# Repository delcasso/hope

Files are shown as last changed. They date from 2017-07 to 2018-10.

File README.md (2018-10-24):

# Welcome to the HOPE project GitHub Page

Here we present and share the full design of a new brain implant.
We believe this implant will be benificial for the community as it is, open-source, cheap, easy to build, easy to modify via CAD software, and 3D printable.

The website is still under construction, please don't hesitate to ask what you need at sebastien.delcasso@gmail.com

To start, look at the [paper](https://www.frontiersin.org/articles/10.3389/fncir.2018.00041/full) and the [contruction protocol](https://github.com/delcasso/hope/blob/master/HOPE%20construction-implantation%20procedure_SD_20180416-1355.pdf).

<br />This work is licensed under a <a rel="license" href="http://creativecommons.org/licenses/by-nc-nd/4.0/">Creative Commons Attribution-NonCommercial-NoDerivatives 4.0 International License</a>.

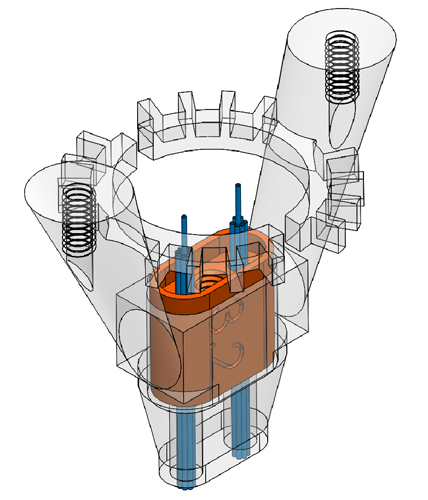
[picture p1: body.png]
body


**Figure 1:** Schematic Representation of HOPE implant

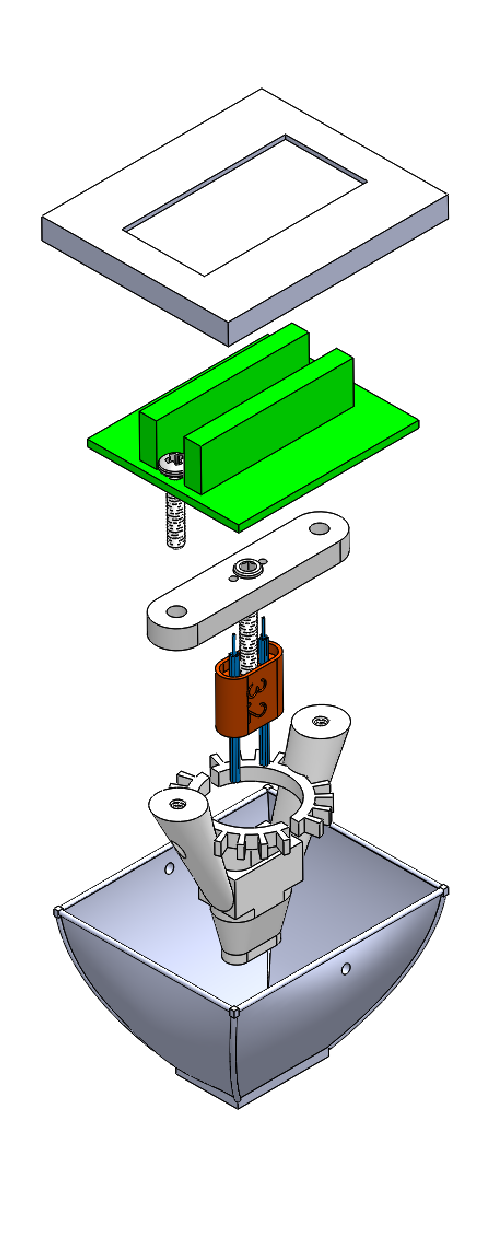
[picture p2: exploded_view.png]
exploded view


**Figure 2:** Exploded View of HOPE implant

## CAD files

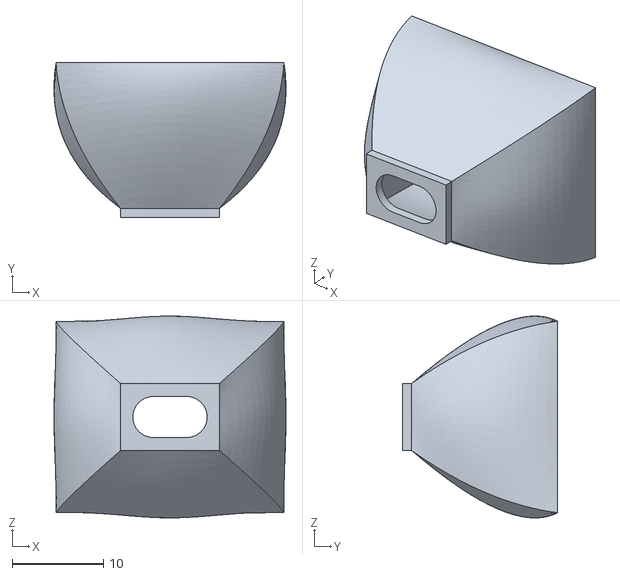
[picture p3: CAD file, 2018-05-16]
CapBottom_20170710.STL
25.4 x 17.0 x 22.2

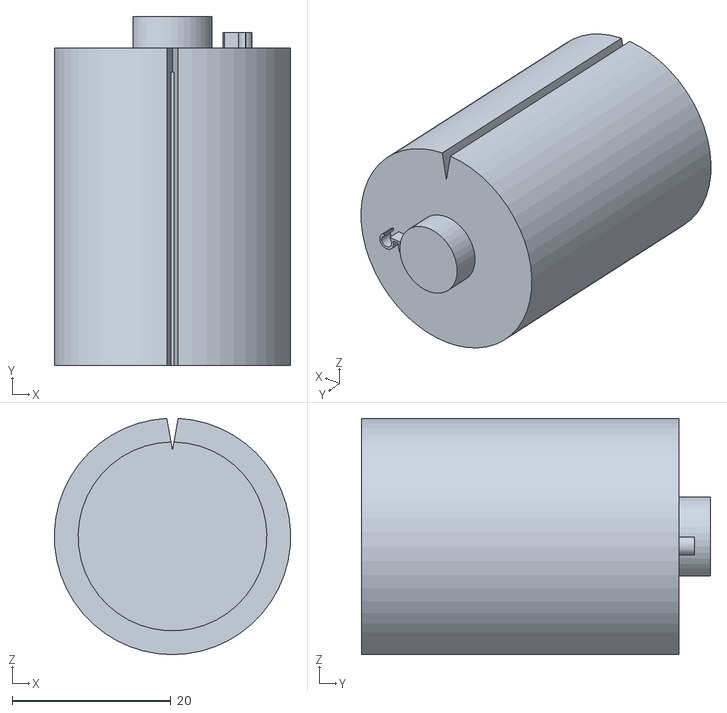
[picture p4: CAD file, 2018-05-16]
length 5mm TetrodeAdjustementPLate^all_20170707.STL
29.8 x 44.0 x 29.8

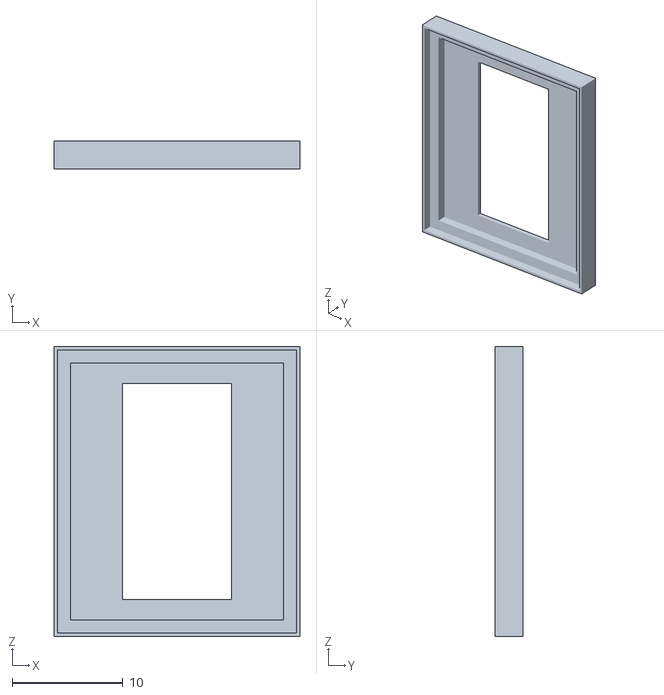
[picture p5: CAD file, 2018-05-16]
CapTop 20170101.STL
22.2 x 2.50 x 26.2

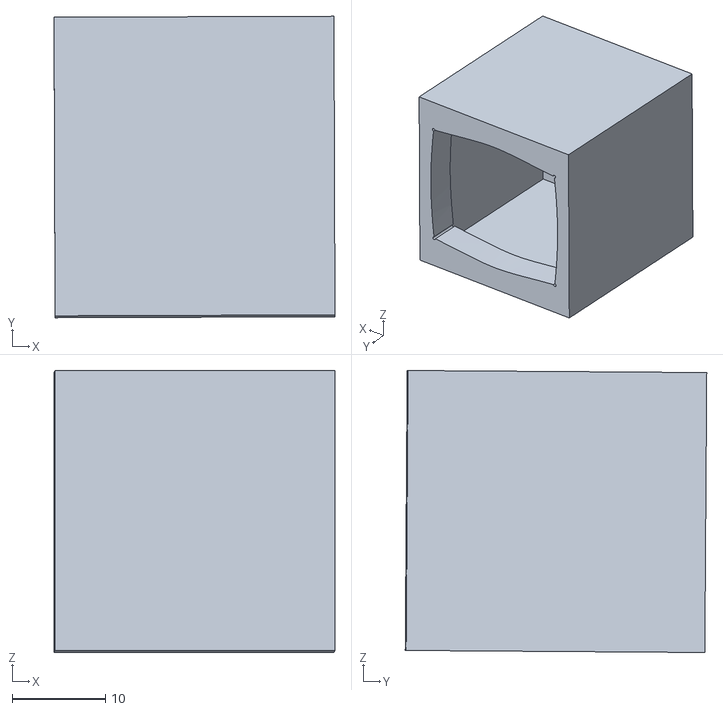
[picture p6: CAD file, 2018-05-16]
StorageBox_20170103.STL
30.1 x 32.3 x 30.2

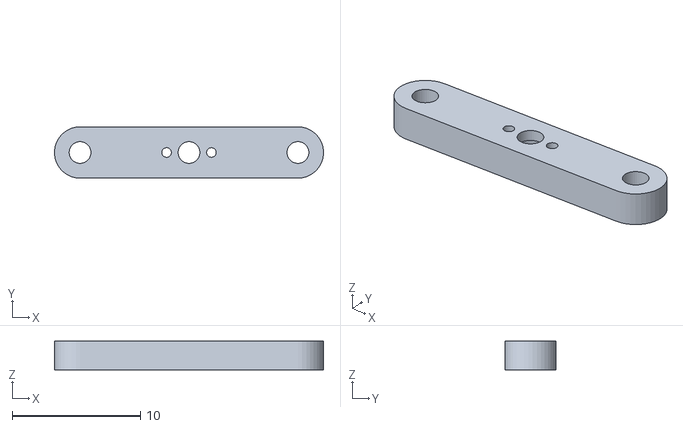
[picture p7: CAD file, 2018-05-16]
Bar_20170101.STL
21.0 x 4.00 x 2.25

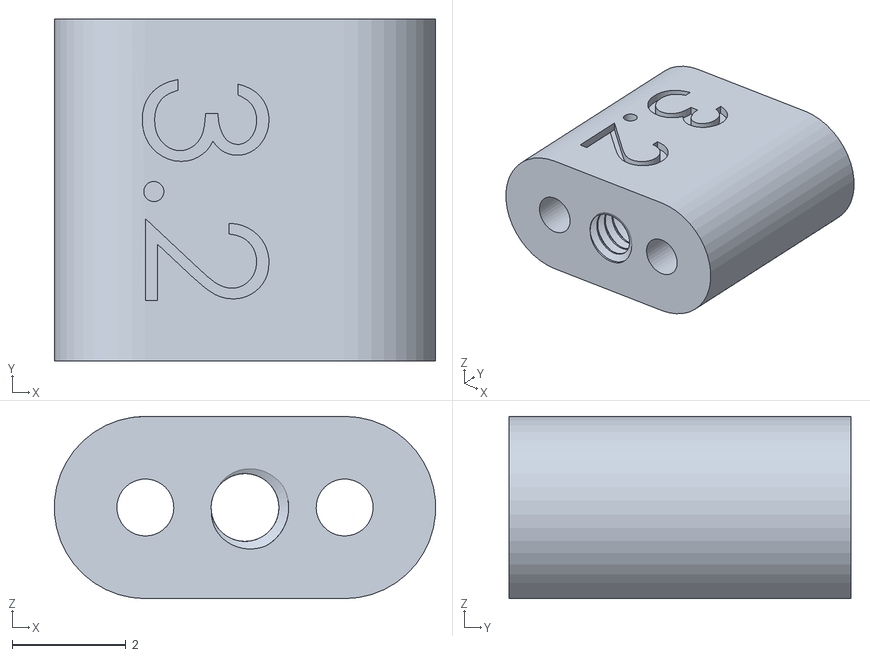
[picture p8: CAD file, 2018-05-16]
3.2 Shuttle.STL
6.69 x 6.00 x 3.20

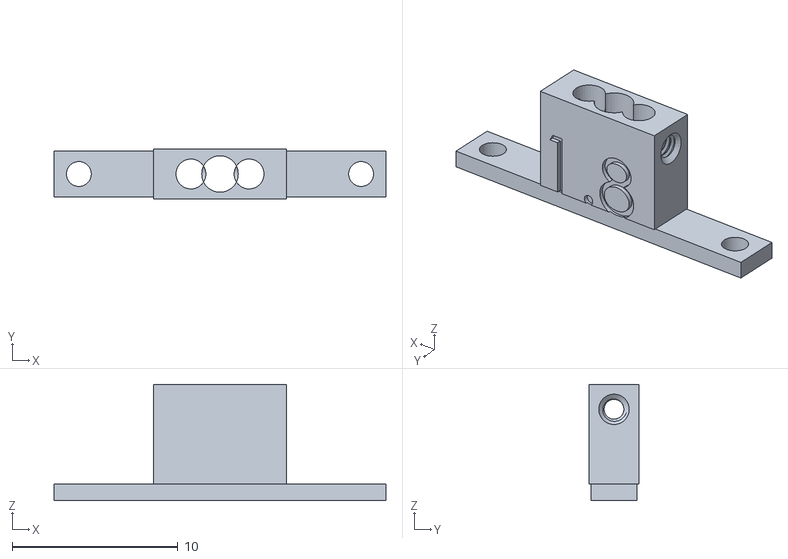
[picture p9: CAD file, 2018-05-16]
FiberHolder 7mm 1.8mm^Assem1.STL
20.0 x 3.00 x 7.00

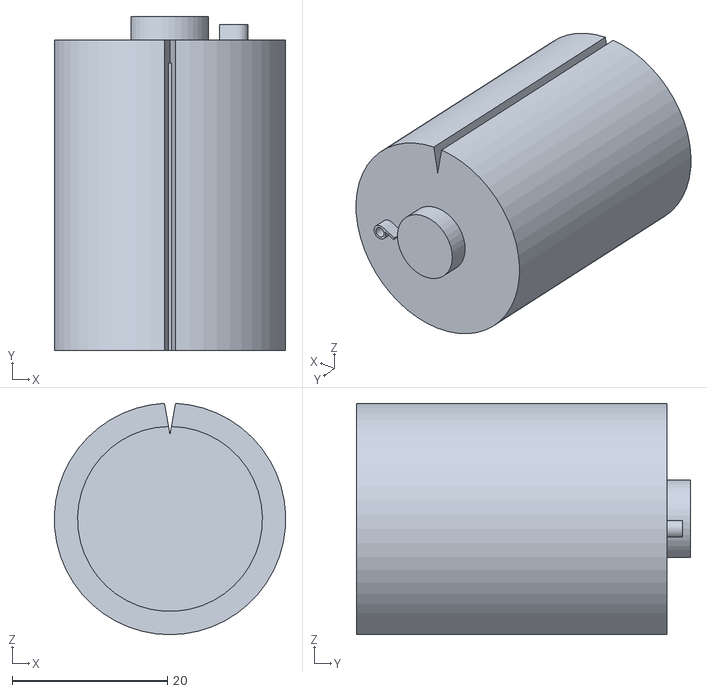
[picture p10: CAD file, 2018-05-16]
length 6mm TetrodeAdjustementPLate^all_20170707.STL
29.8 x 43.0 x 29.8

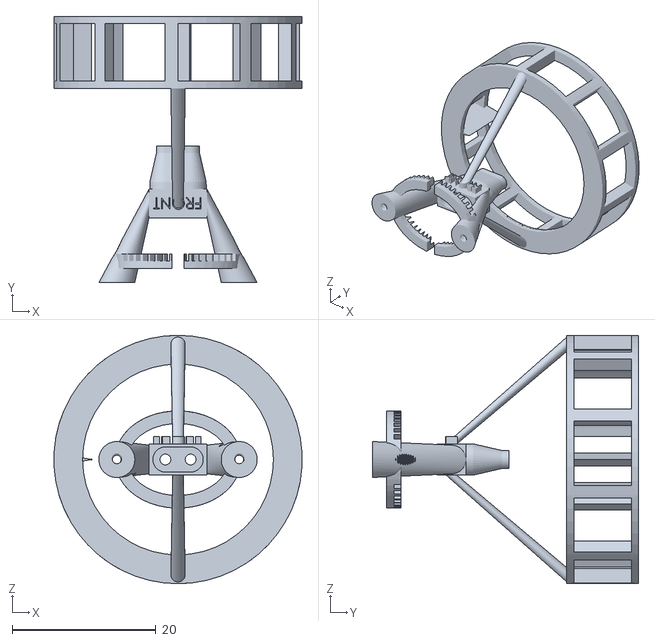
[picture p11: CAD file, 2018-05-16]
Body-With-Stand_20170711.STL
34.4 x 37.0 x 34.5

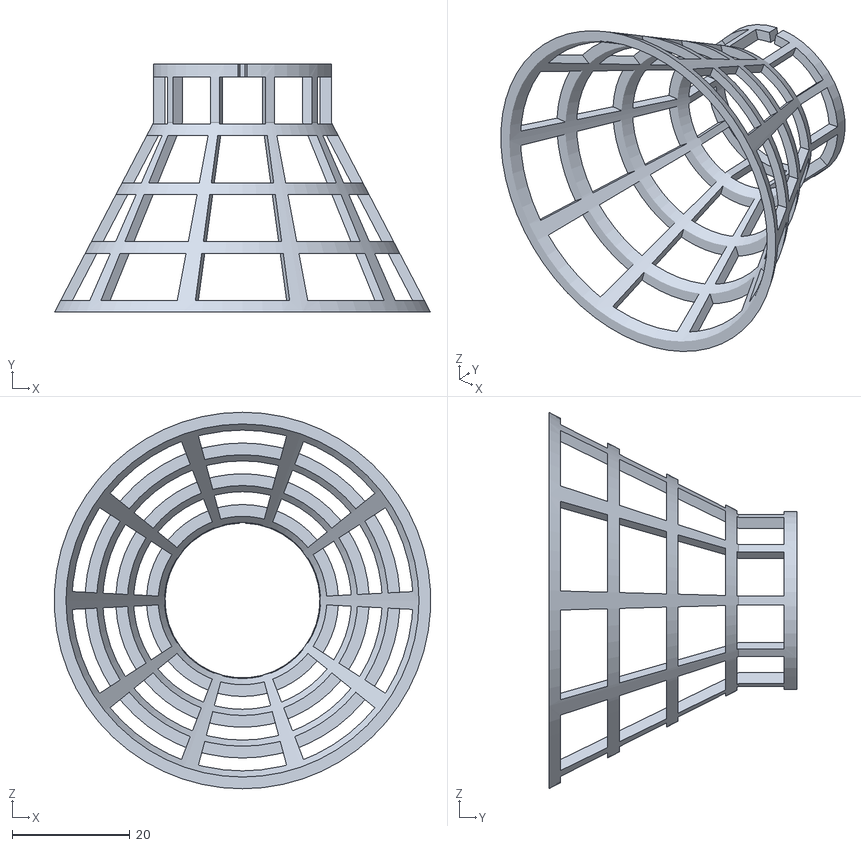
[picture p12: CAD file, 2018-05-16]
TT_loading_stand_20170117.STL
63.9 x 42.2 x 64.0

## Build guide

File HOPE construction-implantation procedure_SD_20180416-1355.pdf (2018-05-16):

FABRICATION OF THE HOPE DRIVE https://delcasso.github.io/hope/

TETRODE FABRICATION

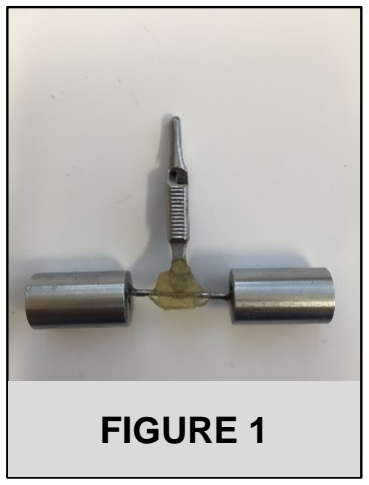
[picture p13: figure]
FIGURE 1

1. Wash your hands.
2. Cut a 30 cm section of 20 µm diameter tungsten wire using serrated scissors.
3. Fold the wire in half and run your fingers along the length of the wire to stick the strands together. Deionized water can be applied if necessary to keep the strands together.
4. Cut the extremity of the loop.
5. Fold the wire in half again to form a loop on one end and cut the tips of the wires on the other end to ensure that they are aligned.
6. Clip the four ends together using an alligator clip that has been modified with a horizontal bar and weights (Figure 1).
7. Hang the wire directly above a turning device and place the bar of the alligator clip into the tetrode spinner (Figure 2).
8. Apply 115 clockwise turns followed by 15 counterclockwise turns.
9. Melt the insulation of the wires to fuse them together. Use a heat gun at the highest temperature setting (1000°F) to heat the wire from four different directions.
10. For each direction, move the heat gun back and forth along the length of
the wire twice at a distance of 1-2 cm, spending approximately 4
seconds on each pass.

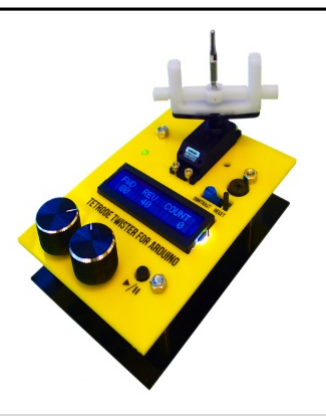
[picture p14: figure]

11. Lift the alligator clip slightly to release the tension from the weights and cut the tetrode above the tip of the alligator clip. Transfer the new tetrode into an anti-static box for storage.

You can consult the following JoVE link for a video that describe the procedures for tetrode construction. https://www.jove.com/video/1098/micro-drive-array-for-chronic-in-vivo-recording-tetrode-assembly (https://www.jove.com/video/1098/micro-drive-array-for-chronic-in-vivo-recording-tetrode-assembly)

### FIGURE 2

SHUTTLE ASSEMBLY

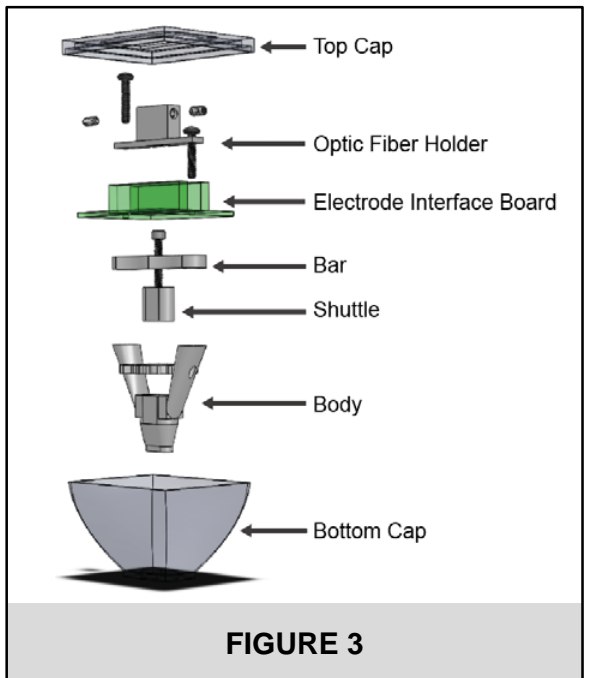
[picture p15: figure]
FIGURE 3

1. Remove all parts from the 3D printer (Figure 3)
2. Remove supports from 3D printed parts (Figures 4 and 5).
3. The shuttle needs to slide smoothly and should be tight inside the body. The shuttle can be sanded down once on each side to ensure a proper fit.
4. Also check that the tetrode adjustment block fit fully within the ring of the body (Figure 6).
5. Use an 0-80 tap to form threads along:
a. the central hole of the shuttle (Figure 7)
b. the two EIB posts on the body
c. the two holes in the side of the body’s shuttle chamber
When you tap the hole, it is not good to try to go all the way in. When it becomes too difficult to turn, it is better to unscrew the tapping tool and blow in the hole.
6. Cut eighteen sections of M-tube (0.0062”/0.0092” ID/OD), each 12 mm in length, with a razor blade.
7. Insert 9 of these segments into both the left and right holes of the shuttle. If you plan to use optical fibers, then cut two more sections of M-tube, each 15 mm in length. Place on long M-tube in the center of each bundle (Figure 8). Optic fibers will be glued inside the middle tube when the bundle will be assembled. If you plan to perform drug injection, place an injection cannula at the center of the bundle. The injection cannula is usually located 500 µm above the tip of the tetrodes.
8. Adjust the position of the M-tubes until they protrude 5.5 mm from the bottom of the shuttle.
9. Apply drops of a light-curing adhesive around the M-tubes using a needle and cure with UV light (405 nm) for 10 seconds. Make sure to wear appropriate glasses to protect your eyes from UV light.
10. Ensure that no adhesive falls into the tapped central hole.
a. It may be easier to make one bundle first and then the other one.

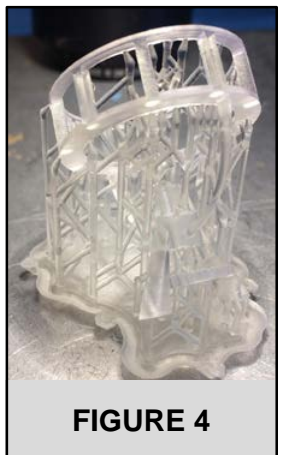
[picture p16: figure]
FIGURE 4
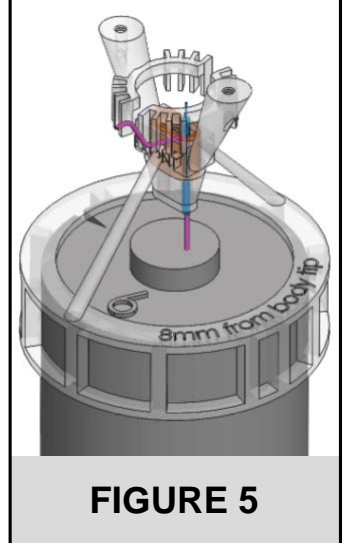
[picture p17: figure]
FIGURE 5
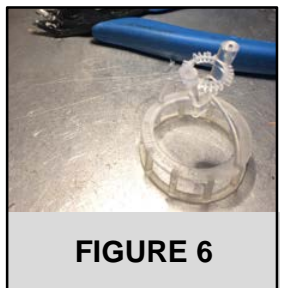
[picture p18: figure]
FIGURE 6
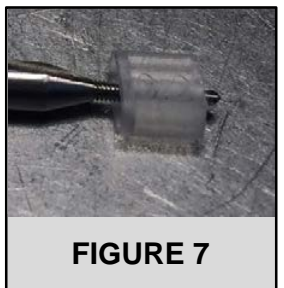
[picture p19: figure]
FIGURE 7

b. Use a needle with epoxy and apply to M-tubes where they exit the base of the shuttle so that the epoxy travels by capillary action up into the shuttle hole and around M-tubes.
c. Apply down about ¾ the length of the M-tubes to ensure each M-tube is secured in the bundle.
11. If necessary, adhesive can be applied slightly above the bottom of the M-tubes to hold them together in a tight cluster. Ensure that no adhesive enters through the bottom of the M-tubes and cure with UV light for 10 seconds. You can also use a second shuttle to hold the tip of the bundle when you are gluing it.

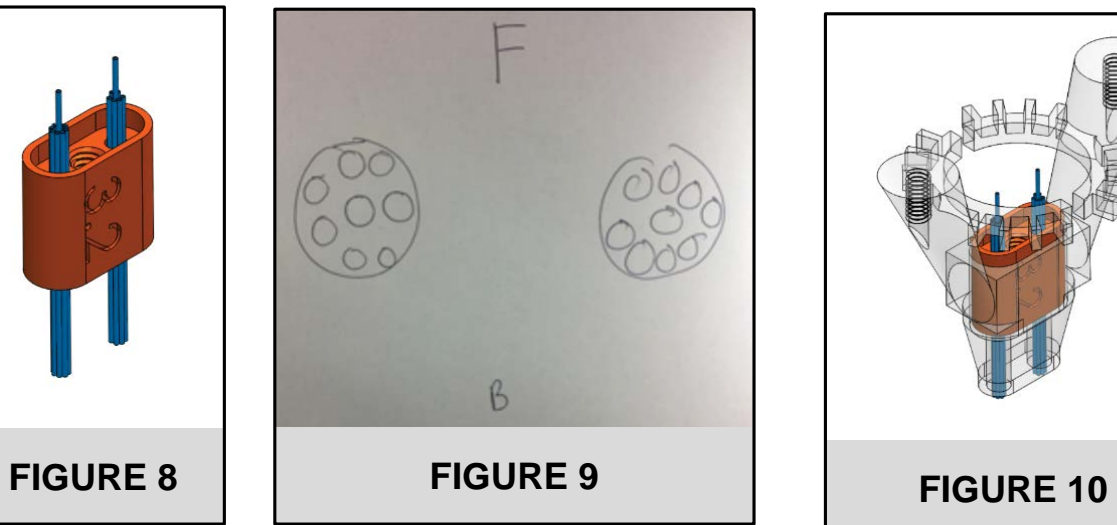
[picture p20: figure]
FIGURE 10 FIGURE 8; FIGURE 9
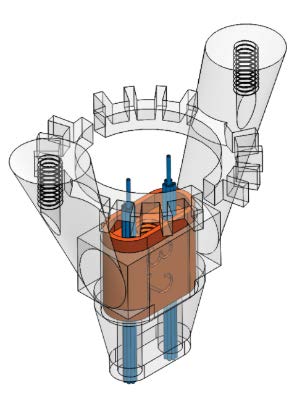
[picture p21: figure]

12. Draw exactly what you see (Figure 9) and label the front side with F (both on the diagram and on the shuttle itself)
13. Use the tap to guide the bottom of the shuttle into the body, making sure that the M-tubes slide through the holes in the drive body without bending. Make sure the shuttle is fully inserted into the body (Figure 10).
14. In preparation for loading tetrodes, with a fine needle (26G), test whether each M-tube is glued in place and does not slide down by touching lightly on the top of each. You can also use a needle to open any compressed M-tube openings.

TETRODE INSERTION

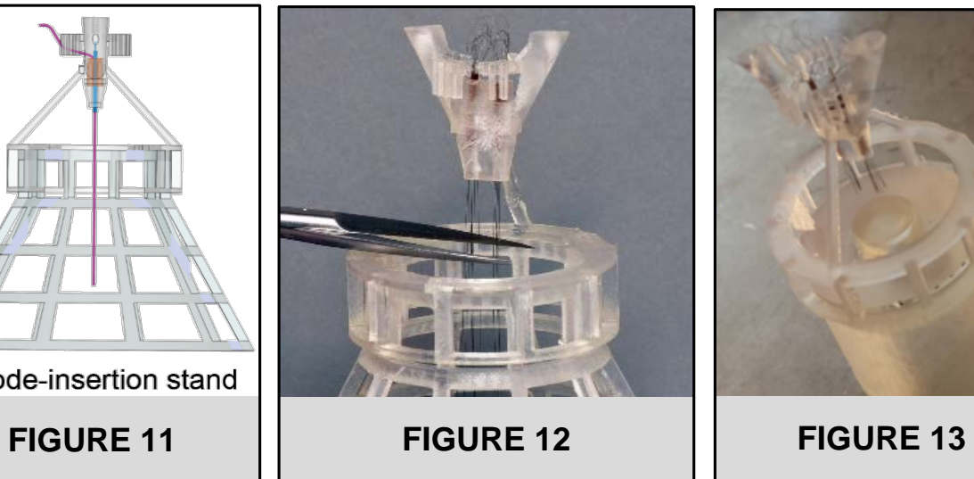
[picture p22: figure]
FIGURE 11; FIGURE 12; FIGURE 13
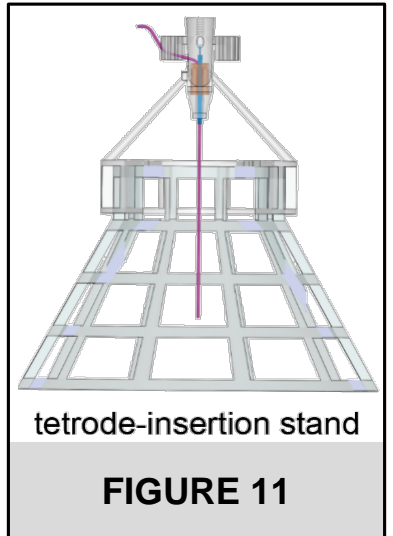
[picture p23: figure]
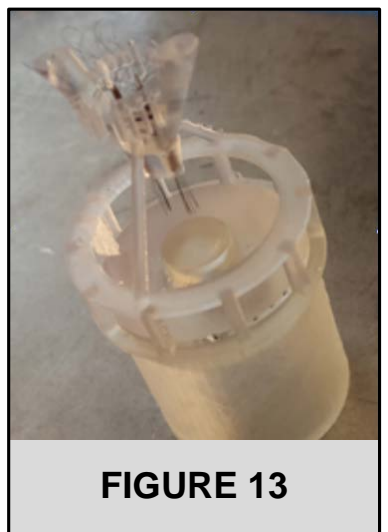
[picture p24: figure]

1. Place drive body into tetrode-insertion stand (Figure 11) and orient under scope. To aid proper orientation, drive frame should have a “Front” label.
a. Orient the “Front” label away from you, facing scope;
b. With this orientation, tetrodes in the left bundle can be loaded and arranged left to right for attachment to EIBs #1 to 8. Right bundle can be loaded and arranged left to right on the bottom ring to attach to EIBs #16 to 9.
2. Insert a tetrode into one of the M-tubes with a pair of forceps. Tap the frame so that the tetrode falls through M-tube. Gently grab the top of the loop at the end of the tetrode, pull up enough to pass it through one of the plastic gates and place it in an appropriate slot (for instance, to reach EIB pin holes #1-4) with ~1.5 cm slack from the slotted ring in order to have enough slack to eventually reach the EIB pins. It is best performed under a microscope.
3. Mark the position of the tetrode order on the diagram.
4. Repeat this process with all sixteen tetrodes and their corresponding plastic gates.
5. With a pair of serrated scissors, cut the tetrodes protruding from the bottom of the body in a single smooth and swift motion across the bottom of the shuttle body and the supporting cylindrical cage of the bottom (Figure 12).
6. Acquire a tetrode length adjuster (Figure 13), and lower the shuttle body and very gently tap the cut tetrode ends on the small cylinder in the tetrode length adjuster until they adjust to be even and flat.
7. Now that the tetrodes have been aligned, they must be secured to maintain their current position inside the M-tubes. Use a needle tip to carefully place a drop of the adhesive above the M-tubes and then cure with UV light for 10 seconds.
8. Important: Maintain awareness not to bend the tetrodes (Figure 14),
and carefully remove the drive from the adjuster and replace it onto
drive frame.
9. Make sure the shuttle has been fully pushed down.
10. Insert the screw into the bar, and then screw in the shuttle until the bar touches the body.

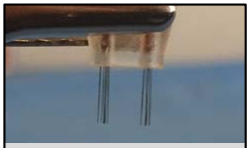
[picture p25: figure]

### FIGURE 14

PREPARATION OF THE ELECTRODE INTERFACE BOARD (EIB)

1. Have an EIB ready.
2. Tap the screw holes on the EIB.
3. Align the bar on the bottom of the EIB using two 0-80 screws.
4. Make a small mark through the center hole of the bar onto the EIB.
5. Make a small hole with a hand drill and a 0.075” diameter drill bit.

MOUNTING THE ELECTRODE INTERFACE BOARD (EIB)

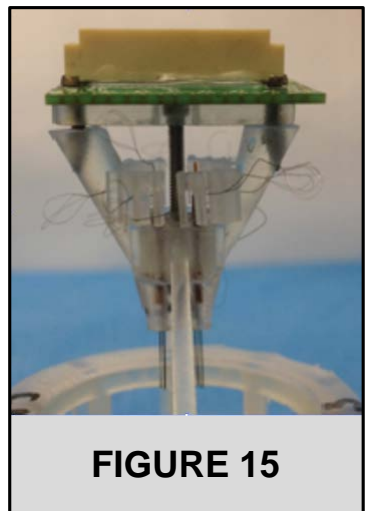
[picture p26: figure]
FIGURE 15

1. Place the electrode interface board onto the posts of the body and use 0-80 x 5/16” screws to secure it in place (Figure 15).
2. Make sure to inspect the EIB and clear any extraneous epoxy from the back that might make the surface uneven; otherwise the printed bar may break. There should not be any gap between the EIB and the bar or between the bar and the body. Tetrode 1 should face the front of the -body, and tetrode 16 should face the back.

ELECTRODE INTERFACE BOARD (EIB)

1. Cut one of the tetrode loops with a pair of serrated scissors to produce four equal lengths of wire.
2. Forceps can be used to gently pull apart the wires if they are stuck together.
3. Each plastic slot on the body corresponds to one of the 16 sets of tetrode holes on the EIB board.
4. Thread the four separated wires of a tetrode through the four corresponding holes on the EIB board above with forceps and secure in place with gold pins.
5. Repeat this process with all sixteen tetrodes.
Forceps quality makes a big difference. We use SPI PTFE-coated#5.
Hold where the four wires meet to avoid bending near the ends (kinks make threading through EIB pin holes more difficult).

GROUND WIRE

1. Cut a 10 cm length of full hardness tungsten wire (0.005” Bare, 0.0070” Coated).
2. Use a torch to burn the insulation off the ends (burn 2 mm on each side).
3. Insert the fold through the ground wire hole (R2) in the EIB, with the longer end directed toward the far side of the device. The wire can be bent slightly so that it remains in place.

PROTECT THE DRIVE

1. Take the 3D printed cap and lower it onto the device. Secure in place by adding drops of light curing adhesive where the body meets the cap and curing with UV light for 10 seconds.

GOLD PLATING

1. Wash the tips of the tetrodes in baths of deionized water, ethanol, and then deionized water again to remove any residue.
2. Attach the fully assembled tetrode device onto the impedance testing apparatus and lower the tips of the electrodes into a bath of gold plating solution. The bath should be connected via a wire to the ground.
3. Open NanoZ on the connected computer and select “Test Impedances.” Initial values typically range from 200 to 400 kΩ.
4. Select “DC Electroplate” and switch to the “Match impedances” mode. The plating current should be set to −0.050 µA with a target of 200 kΩ at 1004 Hz, an interval of 1 second and a pause of 2 seconds. Choose an appropriate number of runs (if your impedances are higher, you will need more runs) and click on “autoplate.”
5. If the number of runs selected was not sufficient to bring the impedance below 200 kΩ, repeat the steps described above until the desired results are obtained. In cases where a tetrode was not connected properly or was constructed poorly, it may not be possible to lower the impedance significantly.

IMPLANTATION

1. Anesthetize the mouse with isoflurane (3% isoflurane in oxygen at 0.8 l/min flow-rate).
2. Shave the head.
3. Head-fix the mouse in a stereotaxic frame.
4. Protect the eyes with ointment.
5. Center the head by adjusting ear-bar positions.
6. Clean the skin three times with betadine followed by 70% alcohol.

7. Make an incision in the skin to expose the calvarium.
8. Insert a sterile plastic ring underneath the skin to maintain the opening.
9. Clean the exposed region.
10. Level the skull using the dorsoventral coordinates of bregma and lambda.
11. Make two shallow openings in the skull with a 0.7 mm drill (AP = +4.0 mm, ML = ±2.5 mm), and stop the drill before the skull was fully perforated.
12. Firmly attach two skull screws to the skull at these two sites.
13. Initiate two craniotomies at AP = 0.85 mm and ML = ±1.75 mm using a large circular drill bit (1.5 mm diameter).
14. Stop the drilling procedure when the skull became very thin.
15. Use a small surgical hook to complete the craniotomy opening.
16. Make an incision in the dura mater using a small 30G needle bent near the tip.
17. Remove the dura mater with fine forceps.
18. Lower the drive that is attached to a stereotaxic arm.
19. Wrap the ground wire around the skull screws, and strengthen the connection using a drop of conductive silver paint on top of the head of the screw.
20. Once the silver paint had dried, cover the screw with a drop of UV-curing glue (Loctite Flash Cure 4311 Cyanoacrylate), and seal the connection with 10 seconds of UV light.
21. Lower the drive extremely slowly into the brain until the tetrodes reached the desired dorsoventral coordinates (−2.5 mm).
22. Finally, attach the HOPE drive to the skull and the skull screws using Metabond quick self-curing cement (Figure 16).

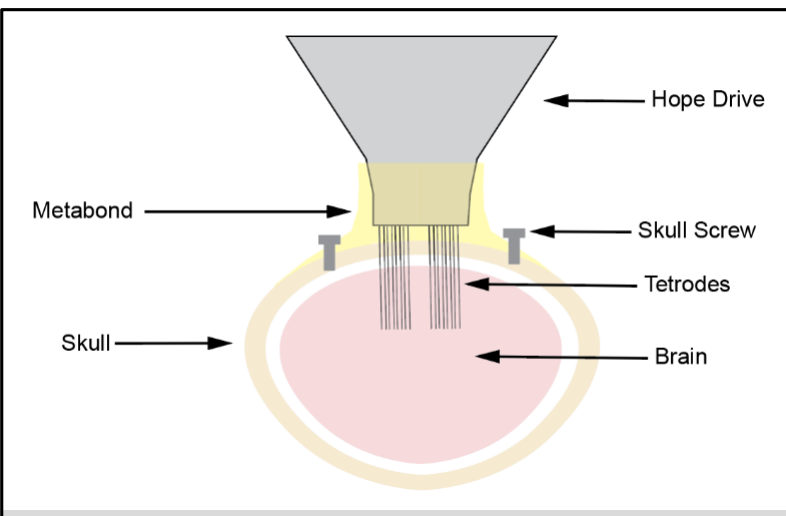
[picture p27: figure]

### FIGURE 16

MATERIALS
- Loctite 4305 Light Cure Instant Adhesive (Henkel, IDH #303389)
- LED-200 UV Spot Curing System (Electro-lite, Part #81172)
- EIB-36-16TT (Neuralynx)
- 8975-6 11.6 AMP 570/1000-Degree Fahrenheit Dual Temperature Heat Gun (Milwaukee Tool Corporation)
- Tetrode Spinner (Neuralynx or open-ephys)
- 8 Micron Tungsten 99.95% CS Wire (California Fine Wire Company)
- Forceps SPI PTFE-coated#5
- 0.0062”/0.0092” ID/OD Medical Grade M-tubing (HPC Medical Products, IWG Lot # 1606000091)
- 3D printed cap, body and shuttle (Formlab Form2 + Clear Resine (GPCL02))
- Small gold plated electrode attachment pins (Neuralynx)
- 320 Grit Sandpaper (McMaster Carr, Part Number 4692A71)
- 0-80 General Purpose Tap (McMaster Carr, Part Number 2522A751)
- 0-80 x 1/8” Stainless Steel Pan Head Machine Screws (McMaster Carr, Part Number 91772A052) (attach EIB through bar to body)
- 0-80 thread size, ½” long, 18-8 stainless steel socket head (middle of the bar) screw (McMaster Carr, Part Number 92196A070).
- 26 GA injection cannula (Plastics One,C315G/SPC)
- 200 µm optic fibers (Thorlabs, CFMXB20)
- Skull screws 0.78 mm diameter (ANTRIN MINIATURE SPECIALTIES, INC.)
